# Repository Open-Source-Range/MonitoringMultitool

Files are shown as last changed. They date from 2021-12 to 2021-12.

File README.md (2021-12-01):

# The Monitoring Multitool

The Monitoring Multi-tool was created as an aid to training crews in how to implement the core methods and as a tool to help ensure high-quality monitoring data are being collected. The Multi-tool has the standard measurement units for implementing the core methods of line-point intercept (LPI), canopy gap intercept, vegetation height measurements, and soil aggregate stability. See below for a descriptions of the Multi-tool features.

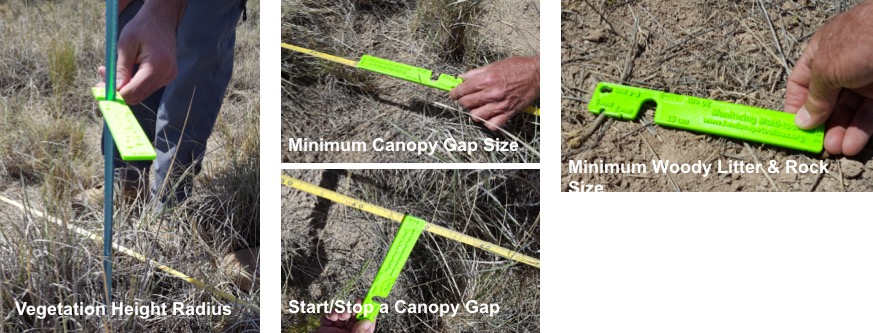
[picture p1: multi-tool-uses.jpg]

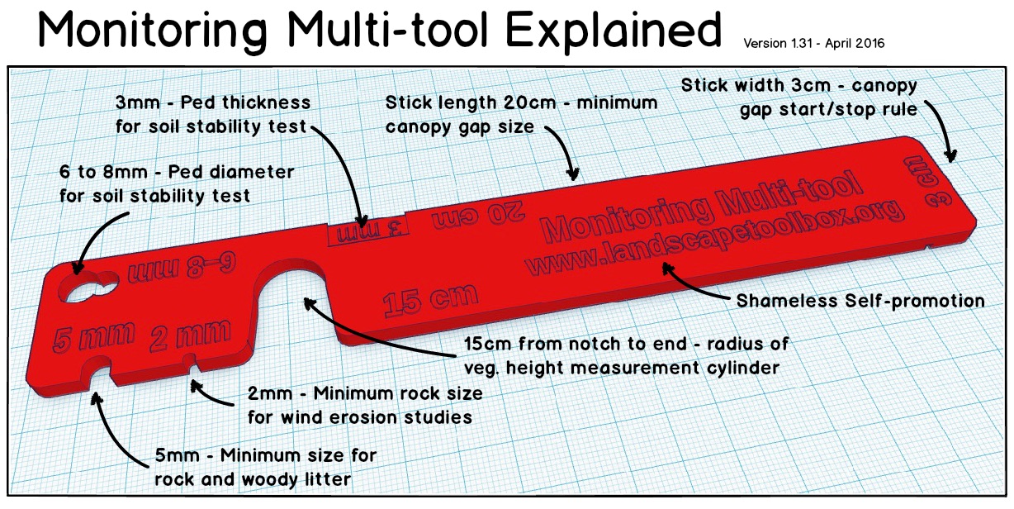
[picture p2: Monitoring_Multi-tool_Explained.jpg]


More information on the Multitool is available at https://www.landscapetoolbox.org/tools/multi-tool/.

Originally the Monitoring Multitools were 3D printed. While this certainly worked, they were not durable enough. With the version 2.0 multitools, we switched to cutting them out of 1/8" (3mm) plywood with a laser cutter. This Repo contains the .STL model files for 3D printing and .SVG files for laser cutting. We used a Full Spectrum Laser Hobby Series laser and FSL's RetinaEngrave software. Cut files for this setup are provided, but unless you have that specific setup, you're probably better off creating your own cut files from the .SVGs.

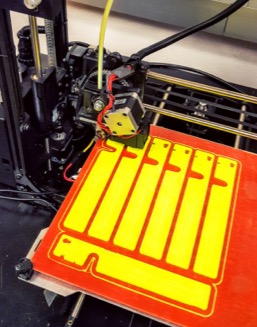
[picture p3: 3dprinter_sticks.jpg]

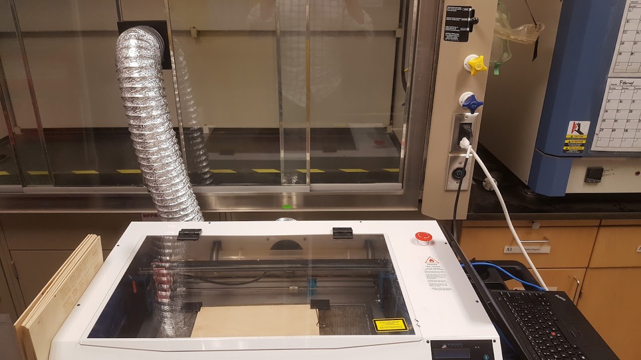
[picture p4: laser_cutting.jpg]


## 3D Model files
 - [multitool_v2.0_body_w_text.stl](./multitool_v2.0_body_w_text.stl) - multitool with text/markings on the front only
 - [multitool_v2.0_body.stl](./multitool_v2.0_body.stl)  - No text on the multitools
 - [multitool_v2.0_body_text.stl](./multitool_v2.0_body_text.stl) - Text and markings only (for if you wanted to do something fancy like embed the text or print it in a different color).

## Laser cutter .SVG files
 - [MTool2-0.svg](./MTool2-0.svg) - Front of multitool, outline and text/markings
 - [MToolv2-0-back.svg](./MToolv2-0-back.svg) - back of multitool, outline and text/markings
 - [MToolv2-0_OutlineOnly.svg](./MToolv2-0_OutlineOnly.svg) - multitool outline only (no text/markings)

#### Multitools laid out to do 9 at a time
Nine multitools on a 12"x12" piece of plywood was the max that would fit on our FSL cutter
 - [MToolv2-0_front_x9.svg](./MToolv2-0_front_x9.svg) - Multitool (w/ text) front
 - [MToolv2-0-back_x9.svg](./MToolv2-0-back_x9.svg) - Multitool(w/ text) back
 - [MToolv2-0_x9_OutlineOnly.svg](./MToolv2-0_x9_OutlineOnly.svg) - Multitool outline only

The [Multitool_Laser_Instructions.docx](./Multitool_Laser_Instructions.docx) file gives instructions for the FSL Hobby Series laser using RetinaEngrave.
The [Monitoring_Multi-tool.zip](./Monitoring_Multi-tool.zip) contains all the .svg files plus the RetinaEngrave cut files for the FSL Hobby-series laser.

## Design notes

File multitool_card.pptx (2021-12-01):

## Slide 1

Monitoring Multitool
Explained

The Monitoring Multi-tool
was created as an aid to training crews in how to implement the core methods and as a tool to help ensure high-quality monitoring data are being collected. The Monitoring Multitool has the standard measurement units for implementing the core methods in the Monitoring Manual for Grassland, Shrubland, and Savannah Ecosystems (2nd Edition).

Version 2.0 – Nov 2016

Standard Measurement Units on the Multitool

Line-point Intercept
- 5mm – Minimum size for rock & woody litter
- 2mm – Minimum rock size for wind erosion studies
Vegetation Height
- 15cm from notch to end – radius of veg height measurement cylinder

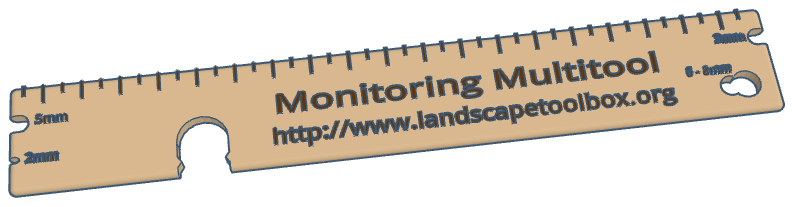
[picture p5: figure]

Canopy Gap Intercept
- 20cm (stick length) – minimum canopy gap size
- 3cm (stick width) – canopy gap start/stop rule
Soil Aggregate Stability
- 6-8mm – Ped diameter for soil stability test
- 3mm – Ped thickness for test
Reverse Side
- Common LPI and unknown plant codes

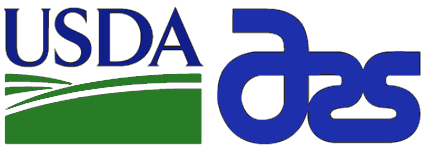
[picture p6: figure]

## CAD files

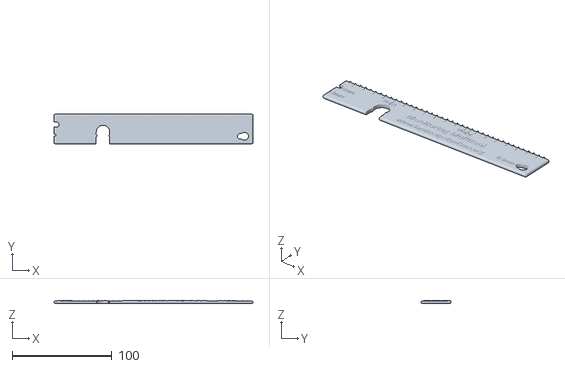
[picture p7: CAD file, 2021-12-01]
multitool_v2.0_body_w_text.stl
200.0 x 30.0 x 3.50

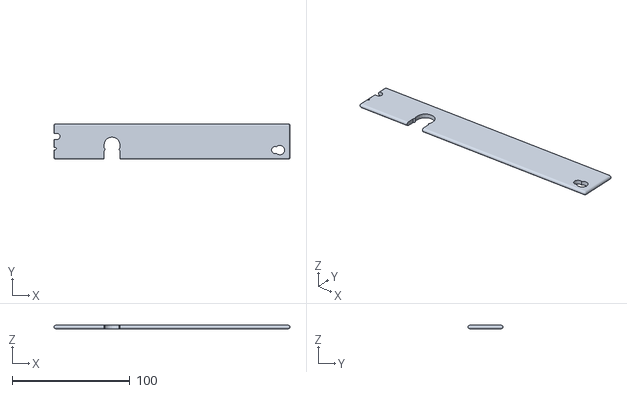
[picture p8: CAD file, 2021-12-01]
multitool_v2.0_body.stl
200.0 x 30.0 x 3.00

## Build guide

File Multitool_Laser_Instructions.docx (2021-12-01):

# Making Monitoring Multitools with the Full Spectrum Laser

## Setting up the laser

1. Roll the laser cart near the fume hood with the laser’s exhaust port nearest to the fume hood.
2. Plug in the white power-strip plug and the computer’s power supply to the outlet on the right side of the fume hood.
3. Hook the laser’s exhaust hose into the glass doors of the fume hood so that the doors stay approximately 4” apart.
4. Turn on the power strip. This will start the exhaust fan, air compressor, and water pump.
5. Look into the laser and see if there are air bubbles circulating through the water jacket in the laser tube. DO NOT OPERATE THE LASER IF THERE ARE LARGE AIR BUBBLES IN THE WATER JACKET. THIS CAN BURN OUT THE LASER TUBE.
6. Push down and turn the red knob on the laser to turn on the laser. The laser will take a few minutes to boot up and acquire an IP address.

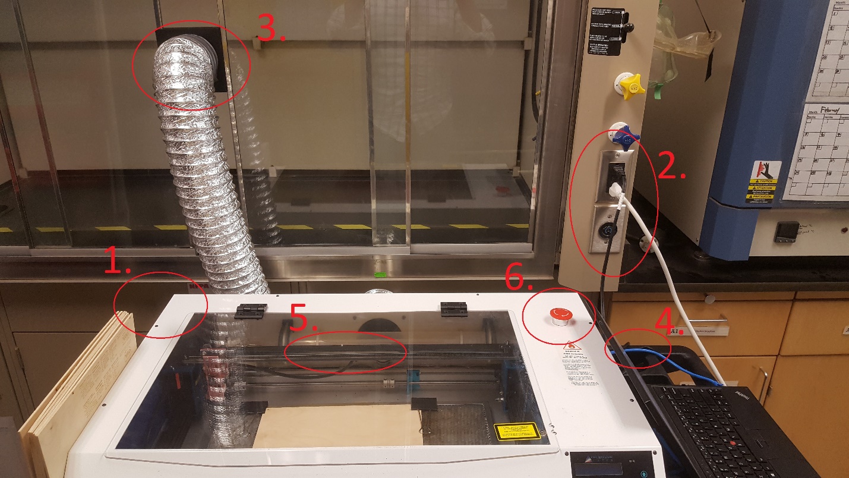
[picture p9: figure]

## Laser Controls

For normal operations, there are two buttons on the laser’s control panel that are useful.

1. The lock/unlock button – frees or locks the laser’s stepper motors. When the motors are free you can move the lens carriage around easily by hand. This is useful for focusing the laser. Lock the motors when you’re finished moving the carriage.
2. The Home button – returns the carriage to the home position.

## Preparing wood for engraving and cutting

1. Monitoring Multitools are cut out 12”x12” pieces of 1/8” plywood.
2. Secure a piece of plywood to the aluminum honeycomb tray using the black binder clips, and either fold down the handles of the binder clips or remove them so they do not interfere with the movement of the lens carriage in the laser.

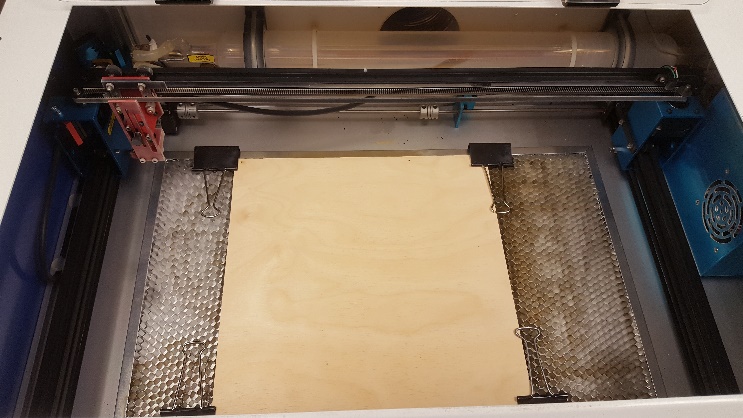
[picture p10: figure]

3. Try to keep the binder clips at close to the edge of the plywood as possible. This will allow for the multitools to be cut close to the edge and maximize the amount of leftover plywood that may be used for other project.

## Engraving/Cutting Monitoring Multitools from RetinaEngrave

1. Double-click on the RetinaEngrave Icon to start the application. Once started, look at the bottom-left corner of the screen and wait until RetinaEngrave connects to the laser and shows the laser’s IP address. Verify that the IP address listed matches the one shown on the laser’s control panel.

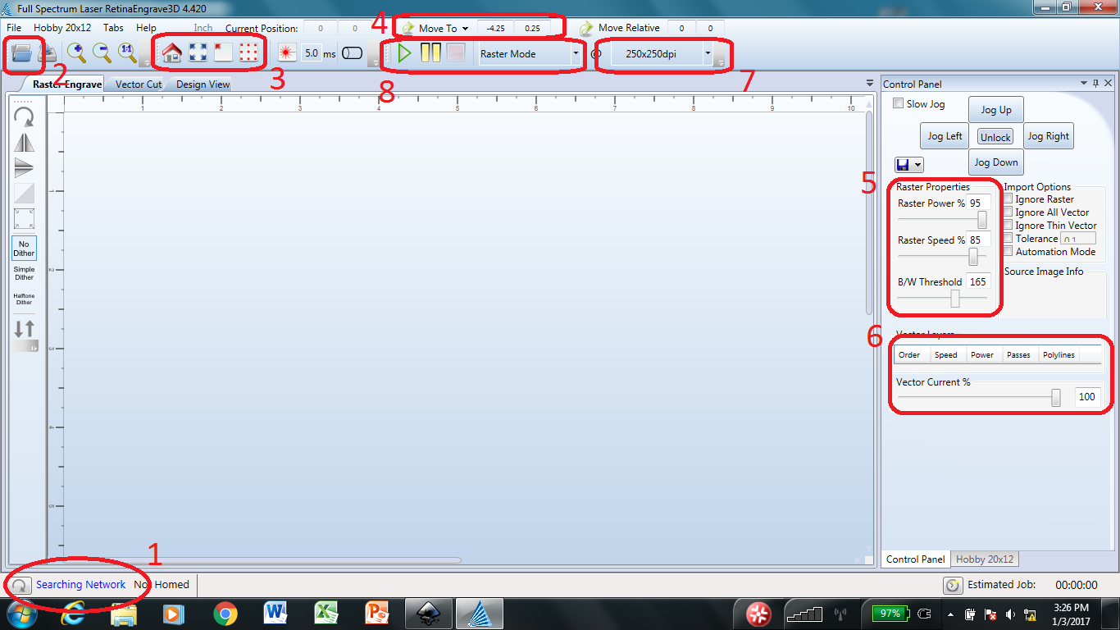
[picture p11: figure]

2. Click the Open icon to open the job file. Select the appropriate .set file and click Open. This will load the cut file and settings into RetinaEngrave. During the load process, you may encounter a message about loading a large raster job. Click Yes to continue.

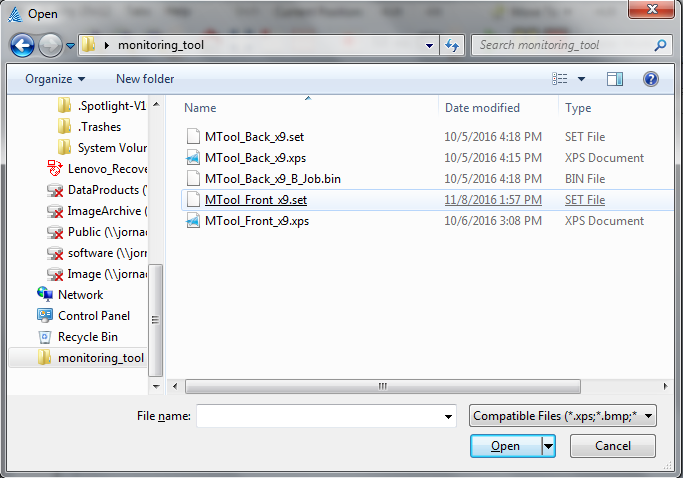
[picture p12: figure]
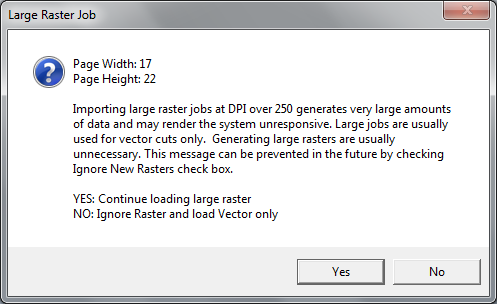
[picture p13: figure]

3. Use the arrow controls on the laser control panel to move the lens (red laser dot) to the upper-left corner of the plywood.  Once the red laser dot is in the correct starting location, use the extent buttons in RetinaEngrave to automatically move the laser lens to the maximum cut extent to ensure that the entire cut stays within the plywood area.
4. You can also move the laser lens from within RetinaEngrave using the Move To button and specifying a location coordinate in inches.
5. Set the raster engrave properties. Raster engrave properties control the intensity and speed of the engraving as well as the color threshold for engraving. Features above the color threshold will not be engraved. Refer to the green stickers on the laptop for optimal settings for engraving either front or back of the multitools.

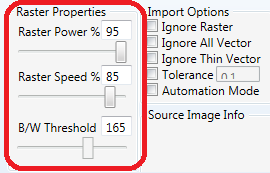
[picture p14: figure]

6. Set the vector cut properties. This controls the intensity of the laser during cutting, the speed at which the lens travels, and the number of cutting passes required. Each color in the original cut file will be included as a different cut line. In this way, you can cut only certain features of the object. Be sure to set the number of passes for objects like multitool text to 0. Again, refer to the green stickers on the laptop for optimal cut settings.
7. Confirm that the raster engrave resolution is correctly set. Some operations in RetinaEngrave can cause this value to be reset. Refer to the green stickers on the laptop for the correct resolution for engraving the multitools.
8. Confirm that the mode is set to Raster then Vector. This tells RetinaEngrave to first engrave the text for the multitools and then to subsequently cut them out. Once the wood and lens are properly aligned, and the correct properties in RetinaEngrave are set, click the Play button (green triangle) to begin engraving/cutting.

## Engraving/Cutting Monitoring Multitools from the Laser Control Panel

The laser saves the last job that it ran. This means that you can rerun the previous job directly from the laser without needing the laptop or RetinaEngrave. This is useful when you need to cut a lot of multitools as you can simply switch out the wood, align it, and start the next batch. This will even work if the laser has been turned off. Once the laser has been turned back on and finished its boot cycle, you can reprint directly from the laser.

1. Follow the steps above for setting up the laser and preparing a piece of wood for cutting.
2. Use the laser control panel arrows to position the lens (red pointer dot) in the upper left corner of the wood.
3. Push the F/S button once, then push the down-arrow button.
4. The LCD display should show, “Run Previous Job?”. Use the down arrow to select “Y”, then press the green checkmark button.

## General Tips and Troubleshooting

The laser is generally very robust and should operate without much problem. The following tips, however, are useful.

- Keep the laptop on and plugged in. The battery in the laptop is old and doesn’t hold a charge. If the laptop is turned off, it takes a long time to boot it back up.
- If the laser is turned off while RetinaEngrave is open, the laser may acquire a different IP address when it boots back up. You can either close and reopen RetinaEngrave or within RetinaEngrave, click on the network refresh button to find the laser again.
- The laser must be properly focused to engrave and cut effectively. If the height of the wood changes, the lens will need to be refocused. Also, the lens will slowly come of out focus over time. Refer to the laser’s operation manual for how to focus the laser. It is easy to do.
- Occasionally wipe down the laser tube and other parts inside the laser using a damp paper towel (wet with water or vinegar solution). Smoke residue builds up inside the laser case.
- Also, occasionally vacuum out the inside of the laser case to keep wood dust and pieces to a minimum. Having a lot of debris in the laser case can be a fire hazard.

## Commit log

2021-12-01 Initial commit
    Create repo, add .stl and .svg files, write some basic documentation.
    [multitool_v2.0_body.stl, multitool_v2.0_body_w_text.stl]
2021-12-01 Add FSL laser cut files
